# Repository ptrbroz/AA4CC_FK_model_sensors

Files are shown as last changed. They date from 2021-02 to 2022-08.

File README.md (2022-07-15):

# AA4CC_FK_model_sensors

FK_quadrature_decoder - DE0-Nano firmware for quadrature decoding and communication. Also includes folders from PC-side communication (python and matlab)

FK_fpga_shield - shield to be placed upon DE0-Nano

FK_encoder_shield - shield to be connected to each incremental encoder

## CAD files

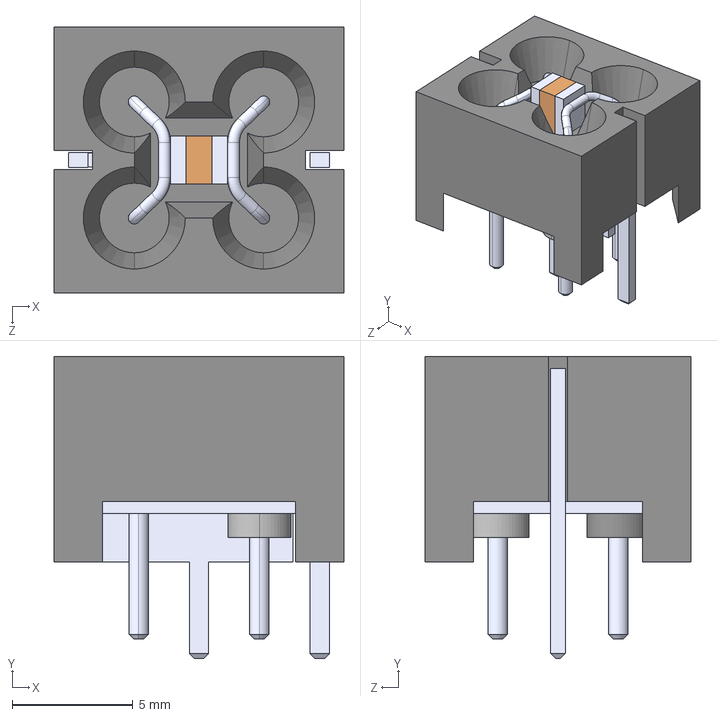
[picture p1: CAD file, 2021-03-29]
FK_fpga_shield/BNX016-01/BNX016-01.step
12.0 x 12.5 x 11.0 mm

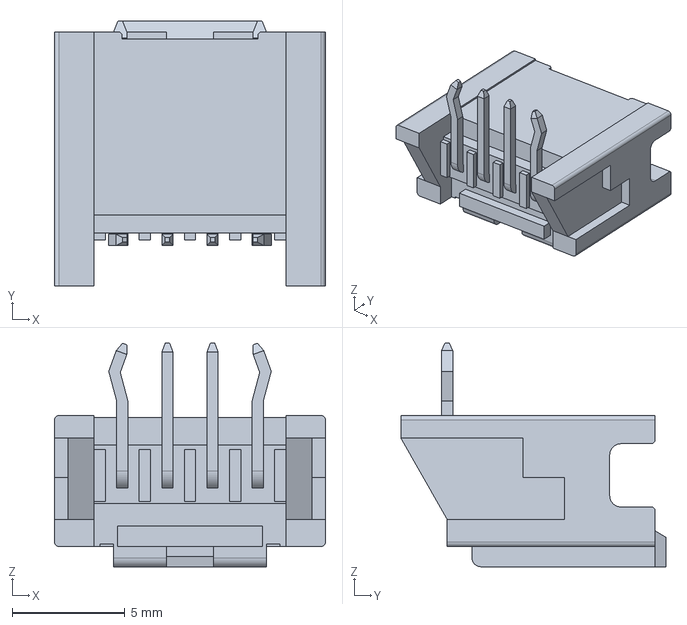
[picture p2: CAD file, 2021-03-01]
FK_fpga_shield/559350430.stp
12.0 x 11.8 x 9.90 mm

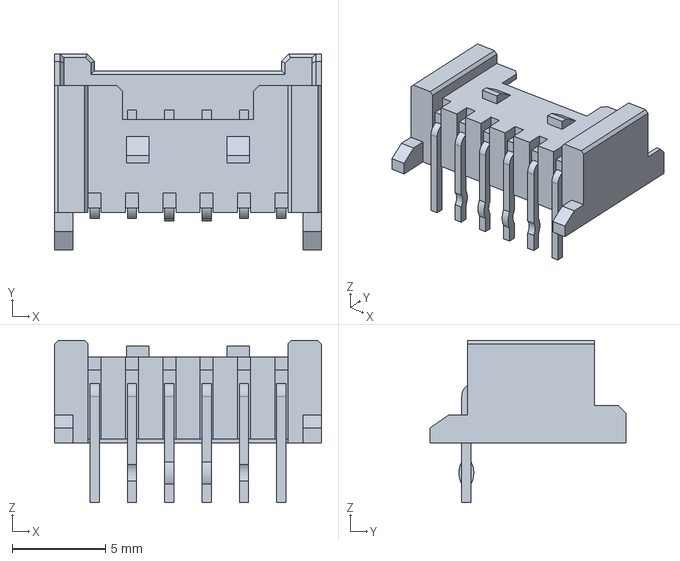
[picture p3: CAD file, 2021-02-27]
FK_fpga_shield/353630660.stp
14.3 x 10.5 x 8.70 mm

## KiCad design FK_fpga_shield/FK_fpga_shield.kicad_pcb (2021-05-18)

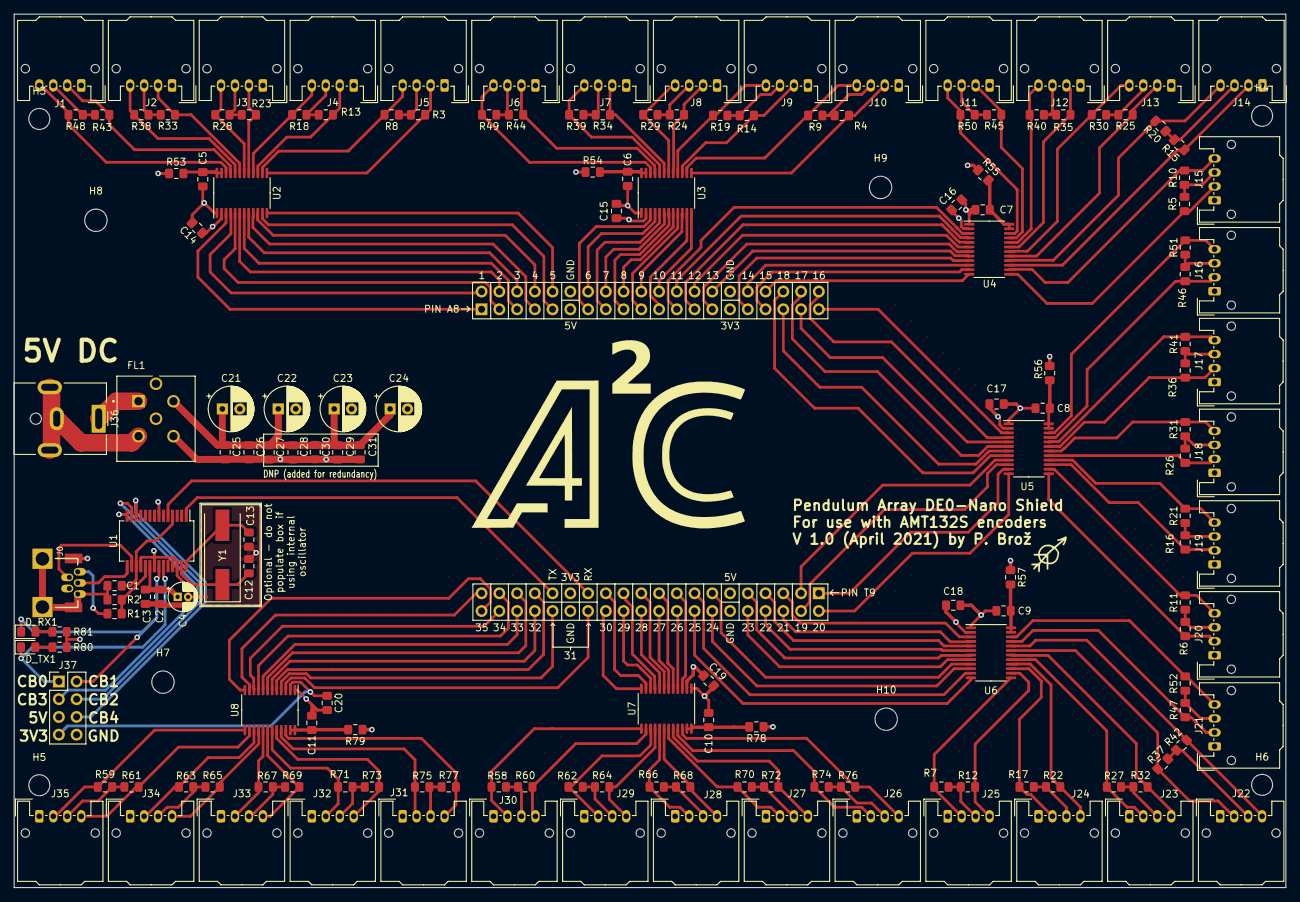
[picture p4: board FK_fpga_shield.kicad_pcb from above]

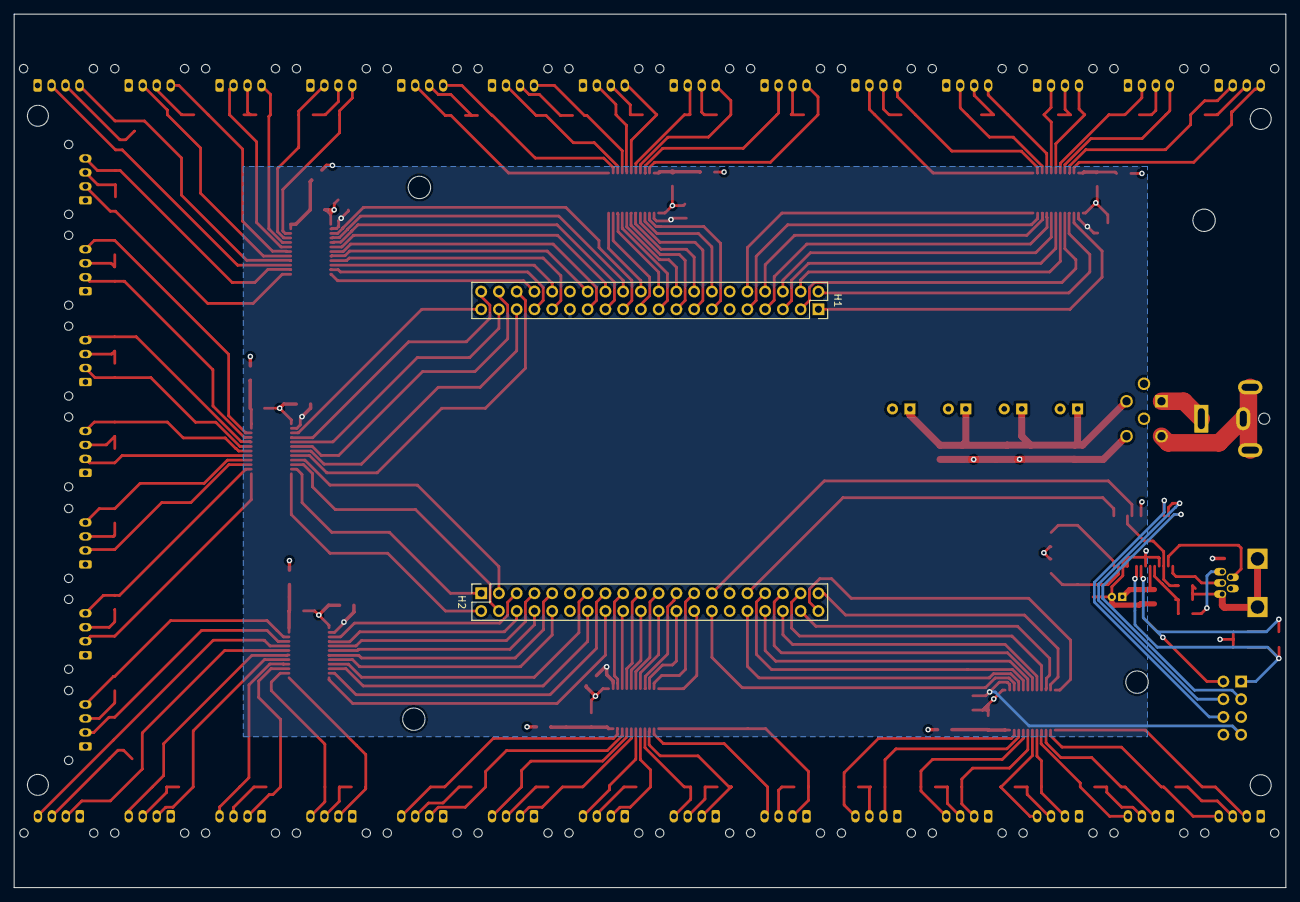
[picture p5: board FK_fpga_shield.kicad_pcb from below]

Board: 4 copper layers, 182.0 x 125.0 mm, 172 parts (2 on the bottom side), 168 nets.

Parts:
C1, C2, C3, C5, C6, C7, C8, C9, C10, C11, C14, C15, C16, C17, C18, C19, C20, C25: 100n; C_0805_2012Metric_Pad1.15x1.40mm_HandSolder
C4: 4.7u; CP_Radial_D4.0mm_P1.50mm
C12, C13: dnp; C_0805_2012Metric_Pad1.15x1.40mm_HandSolder
C21, C22, C23, C24: 22u; CP_Radial_D6.3mm_P2.50mm
C26: 1u_MCC; C_0805_2012Metric_Pad1.15x1.40mm_HandSolder
C27, C28: DNP_10n; C_0805_2012Metric_Pad1.15x1.40mm_HandSolder
C29, C30, C31: DNP_1n; C_0805_2012Metric_Pad1.15x1.40mm_HandSolder
D_RX1: LED RX; LED_0805_2012Metric_Pad1.15x1.40mm_HandSolder
D_TX1: LED_TX; LED_0805_2012Metric_Pad1.15x1.40mm_HandSolder
FL1: BNX016-01; FIL_BNX016-01
H1, H2: Conn_02x20_Odd_Even; PinSocket_2x20_P2.54mm_Vertical
H3, H4, H5, H6: MountingHole; MountingHole_3mm
H7, H8, H9, H10: MountingHole; MountingHole_3.2mm_M3
J0: USB_B_Mini; 54819-0519
J1, J2, J3, J4, J5, J6, J7, J8, J9, J10, J11, J12, J13, J14, J15, J16, J17, J18, J19, J20, J21, J22, J23, J24, J25, J26, J27, J28, J29, J30, J31, J32, J33, J34, J35: molex-51382-0400-microclasp; Molex_MicroClasp_55935-0410_1x04_P2.00mm_Horizontal
J36: Barrel_Jack_MountingPin; BarrelJack_CUI_PJ-063AH_Horizontal
J37: Conn_02x04_Top_Bottom; PinHeader_2x04_P2.54mm_Vertical
R1: 4k7; R_0805_2012Metric_Pad1.15x1.40mm_HandSolder
R2: 10k; R_0805_2012Metric_Pad1.15x1.40mm_HandSolder
R3, R4, R5, R6, R7, R8, R9, R10, R11, R12, R13, R14, R15, R16, R17, R18, R19, R20, R21, R22, R23, R24, R25, R26, R27, R28, R29, R30, R31, R32, R33, R34, R35, R36, R37, R38, R39, R40, R41, R42, R43, R44, R45, R46, R47, R48, R49, R50, R51, R52, R58, R59, R60, R61, R62, R63, R64, R65, R66, R67, R68, R69, R70, R71, R72, R73, R74, R75, R76, R77: 5k6; R_0805_2012Metric_Pad1.15x1.40mm_HandSolder
R53, R54, R55, R56, R57, R78, R79: 200k; R_0805_2012Metric_Pad1.15x1.40mm_HandSolder
R80, R81: 270; R_0805_2012Metric_Pad1.15x1.40mm_HandSolder
U1: FT232RL; SSOP-28_5.3x10.2mm_P0.65mm
U2, U3, U4, U5, U6, U7, U8: nvt2010pw; TSSOP-24_4.4x7.8mm_P0.65mm
Y1: DNP_(12MHz); Crystal_SMD_HC49-SD

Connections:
/1a: H1.2, U2.4
/1b: H1.1, U2.3
/2a: H1.4, U2.6
/2b: H1.3, U2.5
/3V3: C14.2, C15.2, C16.2, C17.2, C18.2, C19.2, C20.1, H1.29, H2.29, J37.7, U2.2, U3.2, U4.2, U5.2, U6.2, U7.2, U8.2
/3a: H1.6, U2.8
/3b: H1.5, U2.7
/4a: H1.8, U2.10
/4b: H1.7, U2.9
/5V: C2.1, C3.1, C4.1, C21.1, C22.1, C23.1, C24.1, C25.1, C26.1, C27.2, C28.2, C29.2, C30.2, C31.2, FL1.2, H1.11, H2.11, J1.3, J2.3, J3.3, J4.3, J5.3, J6.3, J7.3, J8.3, J9.3, J10.3, J11.3, J12.3, J13.3, J14.3, J15.3, J16.3, J17.3, J18.3, J19.3, J20.3, J21.3, J22.3, J23.3, J24.3, J25.3, J26.3, J27.3, J28.3, J29.3, J30.3, J31.3, J32.3, J33.3, J34.3, J35.3, J37.5, R3.1, R4.1, R5.1, R6.1, R7.1, R8.1, R9.1, R10.1, R11.1, R12.1, R13.1, R14.1, R15.1, R16.1, R17.1, R18.1, R19.1, R20.1, R21.1, R22.1, R23.1, R24.1, R25.1, R26.1, R27.1, R28.1, R29.1, R30.1, R31.1, R32.1, R33.1, R34.1, R35.1, R36.1, R37.1, R38.1, R39.1, R40.1, R41.1, R42.1, R43.1, R44.1, R45.1, R46.1, R47.1, R48.1, R49.1, R50.1, R51.1, R52.1, R53.1, R54.1, R55.1, R56.1, R57.1, R58.1, R59.1, R60.1, R61.1, R62.1, R63.1, R64.1, R65.1, R66.1, R67.1, R68.1, R69.1, R70.1, R71.1, R72.1, R73.1, R74.1, R75.1, R76.1, R77.1, R78.1, R79.1, R80.1, R81.1, U1.20
/5a: H1.10, U2.12
/5b: H1.9, U2.11
/6a: H1.14, U3.4
/6b: H1.13, U3.3
/7a: H1.16, U3.6
/7b: H1.15, U3.5
/8a: H1.18, U3.8
/8b: H1.17, U3.7
/9a: H1.20, U3.10
/9b: H1.19, U3.9
/10a: H1.22, U3.12
/10b: H1.21, U3.11
/11a: H1.24, U4.4
/11b: H1.23, U4.3
/12a: H1.26, U4.6
/12b: H1.25, U4.5
/13a: H1.28, U4.8
/13b: H1.27, U4.7
/14a: H1.32, U4.10
/14b: H1.31, U4.9
/15a: H1.34, U4.12
/15b: H1.33, U4.11
/16a: H1.40, U5.4
/16b: H1.39, U5.3
/17a: H1.38, U5.6
/17b: H1.37, U5.5
/18a: H1.36, U5.8
/18b: H1.35, U5.7
/19a: H2.4, U5.10
/19b: H2.3, U5.9
/20a: H2.2, U5.12
/20b: H2.1, U5.11
/21a: H2.6, U6.4
/21b: H2.5, U6.3
/22a: H2.8, U6.6
/22b: H2.7, U6.5
/23a: H2.10, U6.8
/23b: H2.9, U6.7
/24a: H2.14, U6.10
/24b: H2.13, U6.9
/25a: H2.16, U6.12
/25b: H2.15, U6.11
/26a: H2.18, U7.4
/26b: H2.17, U7.3
/27a: H2.20, U7.6
/27b: H2.19, U7.5
/28a: H2.22, U7.8
/28b: H2.21, U7.7
/29a: H2.24, U7.10
/29b: H2.23, U7.9
/30a: H2.26, U7.12
/30b: H2.25, U7.11
/31a: H2.32, U8.4
/31b: H2.28, U8.3
/32a: H2.34, U8.6
/32b: H2.33, U8.5
/33a: H2.36, U8.8
/33b: H2.35, U8.7
/34a: H2.38, U8.10
/34b: H2.37, U8.9
/35a: H2.40, U8.12
/35b: H2.39, U8.11
/RX: H2.27, U1.5
/TX: H2.31, U1.1
GND: C1.2, C2.2, C3.2, C4.2, C5.2, C6.2, C7.2, C8.2, C9.2, C10.2, C11.2, C12.2, C13.2, C14.1, C15.1, C16.1, C17.1, C18.1, C19.1, C20.2, C21.2, C22.2, C23.2, C24.2, C25.2, C26.2, C27.1, C28.1, C29.1, C30.1, C31.1, FL1.4, FL1.5, FL1.6, H1.12, H1.30, H2.12, H2.30, J0.5, J0.6, J1.1, J2.1, J3.1, J4.1, J5.1, J6.1, J7.1, J8.1, J9.1, J10.1, J11.1, J12.1, J13.1, J14.1, J15.1, J16.1, J17.1, J18.1, J19.1, J20.1, J21.1, J22.1, J23.1, J24.1, J25.1, J26.1, J27.1, J28.1, J29.1, J30.1, J31.1, J32.1, J33.1, J34.1, J35.1, J37.8, R2.2, U1.7, U1.18, U1.21, U1.25, U1.26, U2.1, U3.1, U4.1, U5.1, U6.1, U7.1, U8.1
unnamed: C1.1, U1.4, U1.17
unnamed: C5.1, R53.2, U2.23, U2.24
unnamed: C6.1, R54.2, U3.23, U3.24
unnamed: C7.1, R55.2, U4.23, U4.24
unnamed: C8.1, R56.2, U5.23, U5.24
unnamed: C9.1, R57.2, U6.23, U6.24
unnamed: C10.1, R78.2, U7.23, U7.24
unnamed: C11.1, R79.2, U8.23, U8.24
unnamed: C12.1, U1.27, Y1.1
unnamed: C13.1, U1.28, Y1.2
unnamed: D_RX1.1, J37.2, U1.22
unnamed: D_RX1.2, R81.2
unnamed: D_TX1.1, J37.1, U1.23
unnamed: D_TX1.2, R80.2
unnamed: FL1.1, J36.1
unnamed: FL1.3, J36.2, J36.MP
unnamed: J0.1, R1.1
unnamed: J0.2, U1.16
unnamed: J0.3, U1.15
unnamed: J1.2, R43.2, U2.21
unnamed: J1.4, R48.2, U2.22
unnamed: J2.2, R33.2, U2.19
unnamed: J2.4, R38.2, U2.20
unnamed: J3.2, R23.2, U2.17
unnamed: J3.4, R28.2, U2.18
unnamed: J4.2, R13.2, U2.15
unnamed: J4.4, R18.2, U2.16
unnamed: J5.2, R3.2, U2.13
unnamed: J5.4, R8.2, U2.14
unnamed: J6.2, R44.2, U3.21
unnamed: J6.4, R49.2, U3.22
unnamed: J7.2, R34.2, U3.19
unnamed: J7.4, R39.2, U3.20
unnamed: J8.2, R24.2, U3.17
unnamed: J8.4, R29.2, U3.18
unnamed: J9.2, R14.2, U3.15
unnamed: J9.4, R19.2, U3.16
unnamed: J10.2, R4.2, U3.13
unnamed: J10.4, R9.2, U3.14
unnamed: J11.2, R45.2, U4.21
unnamed: J11.4, R50.2, U4.22
unnamed: J12.2, R35.2, U4.19
unnamed: J12.4, R40.2, U4.20
unnamed: J13.2, R25.2, U4.17
unnamed: J13.4, R30.2, U4.18
unnamed: J14.2, R15.2, U4.15
unnamed: J14.4, R20.2, U4.16
unnamed: J15.2, R5.2, U4.13
unnamed: J15.4, R10.2, U4.14
unnamed: J16.2, R46.2, U5.21
unnamed: J16.4, R51.2, U5.22
unnamed: J17.2, R36.2, U5.19
unnamed: J17.4, R41.2, U5.20
unnamed: J18.2, R26.2, U5.17
unnamed: J18.4, R31.2, U5.18
unnamed: J19.2, R16.2, U5.15
unnamed: J19.4, R21.2, U5.16
unnamed: J20.2, R6.2, U5.13
unnamed: J20.4, R11.2, U5.14
unnamed: J21.2, R47.2, U6.21
unnamed: J21.4, R52.2, U6.22
unnamed: J22.2, R37.2, U6.19
unnamed: J22.4, R42.2, U6.20
unnamed: J23.2, R27.2, U6.17
unnamed: J23.4, R32.2, U6.18
unnamed: J24.2, R17.2, U6.15
unnamed: J24.4, R22.2, U6.16
unnamed: J25.2, R7.2, U6.13
unnamed: J25.4, R12.2, U6.14
unnamed: J26.2, R74.2, U7.21
unnamed: J26.4, R76.2, U7.22
unnamed: J27.2, R70.2, U7.19
unnamed: J27.4, R72.2, U7.20
unnamed: J28.2, R66.2, U7.17
unnamed: J28.4, R68.2, U7.18
unnamed: J29.2, R62.2, U7.15
unnamed: J29.4, R64.2, U7.16
unnamed: J30.2, R58.2, U7.13
unnamed: J30.4, R60.2, U7.14
unnamed: J31.2, R75.2, U8.21
unnamed: J31.4, R77.2, U8.22
unnamed: J32.2, R71.2, U8.19
unnamed: J32.4, R73.2, U8.20
unnamed: J33.2, R67.2, U8.17
unnamed: J33.4, R69.2, U8.18
unnamed: J34.2, R63.2, U8.15
unnamed: J34.4, R65.2, U8.16
unnamed: J35.2, R59.2, U8.13
unnamed: J35.4, R61.2, U8.14
unnamed: J37.3, U1.14
unnamed: J37.4, U1.13
unnamed: J37.6, U1.12
unnamed: R1.2, R2.1, U1.19

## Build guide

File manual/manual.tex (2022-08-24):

\documentclass[twoside]{article}
\usepackage[a4paper]{geometry}
\geometry{verbose,tmargin=2.5cm,bmargin=2cm,lmargin=2cm,rmargin=2cm}
\usepackage{fancyhdr}
\pagestyle{fancy}

\usepackage{lmodern}
\usepackage[T1]{fontenc}
\usepackage[cp1250]{inputenc}
\usepackage{amsmath}
\usepackage{amsfonts} 
\usepackage{bm} 

\newcommand\abs[1]{\left|#1\right|}
\newcommand{\res}{\text{res}}
\newcommand{\LH}{\stackrel{LH}{=}}
\newcommand{\FT}{\hat{=}}
\newcommand{\TF}{\check{=}}
\renewcommand\Re[1]{\operatorname{Re}\{#1\}}
\renewcommand\Im[1]{\operatorname{Im}\{#1\}}

\usepackage{url}

\usepackage{multirow}

\usepackage{subcaption}
\usepackage{indentfirst}

\usepackage{graphicx} 
\usepackage{epstopdf}

\usepackage[unicode=true, bookmarks=true,bookmarksnumbered=true,
bookmarksopen=false, breaklinks=false,pdfborder={0 0 0},
pdfpagemode=UseNone,backref=false,colorlinks=true] {hyperref}

\usepackage{xkeyval}	% Inline todonotes
\usepackage[textsize = footnotesize]{todonotes}
\presetkeys{todonotes}{inline}{}

\renewcommand{\theenumi}{\alph{enumi}}

\fancyhf{}
\usepackage{titling}
\fancyhf[HC]{}
\fancyhf[HLE,HRO]{\thetitle}
\fancyhf[HRE,HLO]{\today}

\fancyhf[FLE,FRO]{\thepage}

% �daje o autorovi
\title{FK Quadrature Decoder Manual}
\author{Petr Bro�}
\date{\today}

\begin{document}

\maketitle

\tableofcontents

\newpage

\section{Intro}

This document describes the FK quadrature decoder device, developed at CTU FEE to read an array of up to 35 incremental encoders. The device consists of a DE0-Nano fpga kit, a pcb shield mounted onto the fpga and cables connecting the pcb shield to individual encoders. Both the pcb design and the vhdl code used to program the fpga kit are available from a github repository\footnote{https://github.com/ptrbroz/AA4CC\_FK\_model\_sensors}. 

The document will be split into two parts -- first being a User manual, which will describe how to set up and communicate with the device. It will be followed by a Technical manual, which is meant to aid in extending or modifying the device. It will describe the hardware and cabling, and also roughly sketch out the workings of the fpga program. 

The device uses exclusively positive numbers; when this document uses the word \emph{integer}, interpret it as \emph{unsigned integer} unless explicitly stated otherwise.

\section{User manual}

\subsection{Setting up}

To set up the device, follow theese steps:

\begin{enumerate}
\item If your DE0-Nano is not yet programmed, compile the quartus project and flash it into DE0-Nano. You need to program the serial configuration device, otherwise the program won't persist through a power cycle -- see DE0-Nano user manual for instructions\footnote{https://www.ti.com/lit/ug/tidu737/tidu737.pdf, page 146}.
\item Mount the PCB shield onto the fpga kit. To determine orientation, make sure that the usb connector on the pcb and the usb connector on the fpga kit both point in the same direction. You can also make use of the pcb silkscreen (locations of pins A8 and T9 of the fpga kit are printed on it).
\item Make sure that no usb cable is connected to the fpga kit itself.
\item Connect the incremental encoders to the connectors located at the edges of the pcb shield.
\item Connect a 5V DC power source via the barrel jack.
\item Connect the pcb shield to your computer via the mini-usb port located next to the barrel jack.
\end{enumerate}

\subsection{Turning off the device}
\label{turnoff}

Ideally, when turning off the device, unplug the usb cable first and only then unplug the 5V power adapter.

Alternatively, it is enough to turn off the computer to which the usb cable is connected instead of unplugging it (if the usb port to which it connects turns off with the computer).

Due to an oversight in the pcb design, unpluggin the 5V power source while a usb cable is connected places the FT232R (uart-usb converter) chip outside its maximum ratings. 

A solution (which eliminates the need to unplug cables in specific order) to this oversight is described in \ref{hwbug}.

\newpage{}

\subsection{Communication}

\par The device communicates with the user via bidirectional UART with following parameters: Baudrate 230400, 8 data bits, no parity. Apart from going to the usb-serial converter IC, the fpga's transmit line is also routed to pin B16 (located on the bottom gpio header)\footnote{I reccomend this site for locating pins on DE0-Nano: https://sites.google.com/site/fpgaandco/de0-nano-pinout} where a oscilloscope probe can be attached for inspection.

Upon powerup, the device will not be sending any data -- it needs to be configured first.

\subsubsection{User to device communication}

There are three types of commands the user can send to the device. Two of them consist of only a single byte that the user needs to send:

\begin{enumerate}
\item \textbf{COMMS ON} -- sending the byte 0x04 causes the device to start transmitting data, using it's current settings.
\item \textbf{COMMS OFF} -- sending the byte 0x02 causes the device to stop transmitting data.
\item \textbf{CONFIGURE} -- see below.
\end{enumerate}

The \textbf{CONFIGURE} command consists of 7 bytes. It is used to choose which encoders will be reported by the device, at what resolution, how often, and lastly it allows the positions of the encoders to be reset. Upon receiving the configure command, the device will send a reply (see next section), reconfigure itself and start transmitting data.

The first nibble of the first byte encodes the desired revolution counter bit-depth. When set to 0, the device does not report the number of revolutions. The second nibble of the first byte must be 0x1. 

The remaining 6 bytes are best thought of as an array of bits. The first 35 bits form the encoder enable vector -- when a bit in the enable vector is set to one, the corresponding encoder's position (and possibly number of revolutions) will be reported\footnote{The encoder connectors on the pcb are enumerated clockwise, starting next to the barrel jack. Their numbers are also printed on the silkscreen as JX, where X is the number.}. Bits 36 to 39 form an unsigned integer, used to represent the desired position resolution in bits. Bit 40 is the position  reset bit -- when it is set to one, all positions will be reset to their default value of $2^{r-1}$, where $r$ denotes the position resolution in bits. The last 8 bits form another unsigned integer, this time representing the minimum time the device should wait between sending its messages, in milliseconds.

\textbf{Example: Configure command}

\begin{figure}[htb]
	\centering
	
	\caption{Configure command illustration}
	\label{fig:config}
\end{figure}

The figure on this page illustrates how the configure command is assembled. The values show therein are choosen to configure the device to:

\begin{itemize}
\item Set revolution counter bit depth to 5 bits
\item Enable reading encoders 1 through 10 and 26 through 35
\item Disable reading encoders 11 through 25
\item Read them using a resolution of 12 bits
\item Reset the position counters.
\item Transmit data once every 10 milliseconds.
\end{itemize}

To achieve theese settings, the user needs to send following bytes (in this order) to the device: 0x51, 0xFF, 0xC0, 0x00, 0x7F, 0xF9, 0x0A.

\subsubsection{Settings constraints}

Following settings are valid:

\begin{itemize}
\item \textbf{Encoder enable vector} -- Any combination of ones and zeros.
\item \textbf{Position resolution} -- Any integer from 1 to 13. If a zero is sent, it will be interpreted as one. 13 is the maximum resolution used within the device -- while resolution options of 14 and 15 bits are also supported, they only pad the sent data with zeros and you shouldn't use them unless you know exactly why you're doing it. (See TODO)
\item \textbf{Revolution counter bit depth} -- Any integer from 0 to 7. Setting a zero disables revolution reporting altogether. If a value greater than 7 is sent, it will be reduced to 7.
\item \textbf{Reset bit} -- Either 1 or 0.
\item \textbf{Minimum time between messages} -- Any integer between 0 and 255. Be aware that this is the minimum time -- the actual time between messages will always be at least as long as it takes to transmit all the data. Formula for minimum time it takes to transmit (assuming revolution data is not sent): $(ceil(\frac{(r+1)\cdot{}E}{8}) + 3)\cdot{}\frac{10}{B}$, where r is resolution in bits, E is the number of enabled encoders and B is Baud = 230400. If revolution data is enabled, the minimum time will increase to  $(ceil(\frac{4+(r+R+2)\cdot{}E}{8}) + 3)\cdot{}\frac{10}{B}$, where R is the revolution counter bit depth.
\end{itemize}

\subsubsection{Device to user communication}

The device can send two types of messages to the user. Both begin with a header consisting of 3 bytes and are then followed by a number of data bytes. Reserved separator bits are inserted into the data to ensure that the byte pattern of a header does not occur within the data -- allowing for clear identification of the beginning of a message in incoming bytes.\footnote{This rule is broken if you set the resolution to 14 or 15 bits.} \\

\noindent\emph{\textbf{Configure reply message}}

This message is sent only as a reply to the configure command sent by the user. It's header always consists of bytes 0xff, 0xff, 0xf0 in this order. Following them are 7 data bytes -- those carry within them the same array of 48 bits that the user provided in their configure command, with the exception that the first bit of each data byte is instead reserved as a separator bit and is always zero.

The configure reply message does not currently report the revolution counter bit depth.

\textbf{Example: Config reply message}
\begin{figure}[h!]
	\centering
	
	\caption{Configure reply illustration (Only first 5 bytes are shown)}
	\label{fig:JpgEpsCompare}
\end{figure}

The figure above illustrates how a reply to the configuration reply message to the message show in figure \ref{fig:config} would begin. \\\\

\noindent{}\emph{\textbf{Data message (without revolutions)}}

This section assumes that revolution counter bit depth is set to zero, meaning that revolution data is not reported by the device. See below for how the message changes when revolutions are reported.

This is the most important message -- it is used by the device to report the positions of encoders to the user.

The header of this message is a little more complex, as it carries data. Its first byte is always 0xff, its second byte is one of \{0xfc, 0xfd, 0xfe, 0xff\}, and its last byte can have many different values. When viewed as an array of 24 bits, it can be parsed thus:

\newpage{}
\begin{itemize}
\item Bits 1 to 14 -- Reserved, will always be ones.
\item Bits 15 to 20 -- Integer representing how many encoders are enabled
\item Bits 20 to 24 -- Integer representing the resolution in bits
\end{itemize}

The purpose of the reserved bits is to facilitate identification of the beginning of the message. Due to presence of separator bits (which are always zero) and maximum position resolution being 13 bits, the only situation in which 14 consecutive ones appear in data sent by the device is a message beginning.

The header is followed by a number of data bytes, which carry the positions of each enabled encoder. Each position is sent as an integer preceded by a separator bit (which will always be zero). Thus the number of bytes you should expect can be calculated after parsing the header as $ceil(\frac{(r+1)\cdot{}E}{8})$, where r is resolution in bits and E is the number of enabled encoders. The positions are sent starting in ascending order of encoder indices.

The number of encoders and resolution should fall within certain constraints. In particular, the number of enabled encoders needs to be at most 35, and the resolution needs to be between 1 and 15 bits, otherwise the 3 bytes do not form a valid data message header. Note that the header for Config reply message appears as 63 encoders running at resolution of zero bits, and thus can be differentiated from data message headers.

\textbf{Example: Data message (revolution reporting disabled)}
\begin{figure}[h]
	\centering
	
	\caption{Data message illustration}

\end{figure}

Figure above shows what a data message might look like. Upon parsing the header, the user computer performs the calculation $\frac{(6+1)\cdot{}3}{8} \approx 2.6$. Rounding (always) up, we arrive at 3 -- the number of data bytes we need to receive. The last 3 bits of the third data byte do not carry any information.

Reading the positions, we see that the third encoder is in the default position, encoder number one has moved somewhat in one direction from the default and number two has moved significantly in the opposite direction.

Note that there is no indication of the actual index of the encoders -- the user needs to keep in mind which encoders they have enabled. The message above might represent the positions of encoders 1, 2 and 3. But it may also represent the positions of encoders 5, 26 and 31, if those happen to be the ones that are enabled.

\noindent{}\emph{\textbf{Data message (with revolutions reported)}}

Currently, it is not possible to differentiate between data messages with revolutions and without revolutions based just on the initial header. It is recommended for the user to note if they configured revolution counter bit depth to a nonzero value and to expect messages with revolution data if they did so.

When revolution counter bit depth is nonzero, the positions data is followed by a section of revolution data. The data section is the same as in case of data message without revolutions (see above).

The revolution data section begins with a secondary header consisting of 4 bits which encode the revolution counter bit depth used. Following the header is an array of bits in a similar format to the positions section: each revolution counter is preceded by a separation bit (always zero). Thus revolutions reporting prolongs the data message by 4+(1+R)*E bits, where R is is the revolution counter bit depth and E is the number of encoders.

The total number of bytes of the data message with revolutions is calculated as  $ceil(\frac{4+(r+R+2)\cdot{}E}{8})$, where r is the position resolution. 

Revolutions are represented as integers with offset zero. No revolutions corresponds to a value of $2^R$. This value is incremented whenever the position of the encoder in question overflows and decremented whenever it underflows.

\begin{figure}[h]
	\centering
	
	\caption{Data message illustration}
\label{fig:3}
\end{figure}

Example message is shown in figure \ref{fig:3}. Note that due to the zero offset, counter value of 6 for encoder 1 should be interpreted as that encoder performing a sum of two revolutions in one direction, while encoder 2 (counter value 3) has performed a sum of one revolution in the opposite direction. A counter value of 4 would correspond to a sum zero revolutions.

\newpage{}
\subsection{Communications demo}

\noindent{}A terminal demo script written in python is located within this repository:\\ FK\_quadrature\_decoder\textbackslash{}python\textbackslash{}CommDemo.py.

The script consists of utilities for conversion between bytes and lists of bits, as well as a function that initialises the device with desired settings and another that parses its reply. The parsing of data messages is done in a loop in the program itself.

When using the script, you may experience bytes being discarded if you set the minimum time between messages too low. In my testing, this problem appeared to be closely related to the ammount of information printed into the terminal, as well as to whether my pc was performing other intensive operations, and would lessen or disappear altogether when I redirected the script's output into a log instead of printing it to terminal. This leads me to believe that it is a fault of the computer rather than of the device; I'm guessing it's caused by a buffer overflowing somewhere. 

The script also does not (at the time of writing) check for validity of incoming data message headers.

The script was tested on windows 10 machines, using Windows Terminal\footnote{https://github.com/microsoft/terminal} (default windows cmd does not support the return codes needed to redraw multiple lines of data).

\subsection{Reconfiguring on the fly}

As a last note: the device keeps count of the positions of all  encoders at all times; not just the ones that are currently enabled for reporting. You can, therefore, begin your experiment with only some of the encoders enabled and switch to a different set of enabled encoders later -- no position reset is necessary.

\newpage{}
\section{Various technical details}

You don't need to read any further unless you're planning to modify or extend the firmware or hardware of the device.

\subsection{Cabling}

The cable used for interconnecting the pcb shield and the AMT132S encoders is 24AWG, 4-wire UTP. Wire gauge selected as only intersection that's within specs of crimp terminals on both sides.

The cable is terminated with a microclasp connector on one side and a zpd connector on the other. Since the encoders use a 18-path zpd connector (which was not available for purchase), 20-path zpd connectors cut down with a hobby knife are used instead.

\begin{figure}[h!]
	\centering
	\begin{subfigure}[b]{0.45\textwidth}
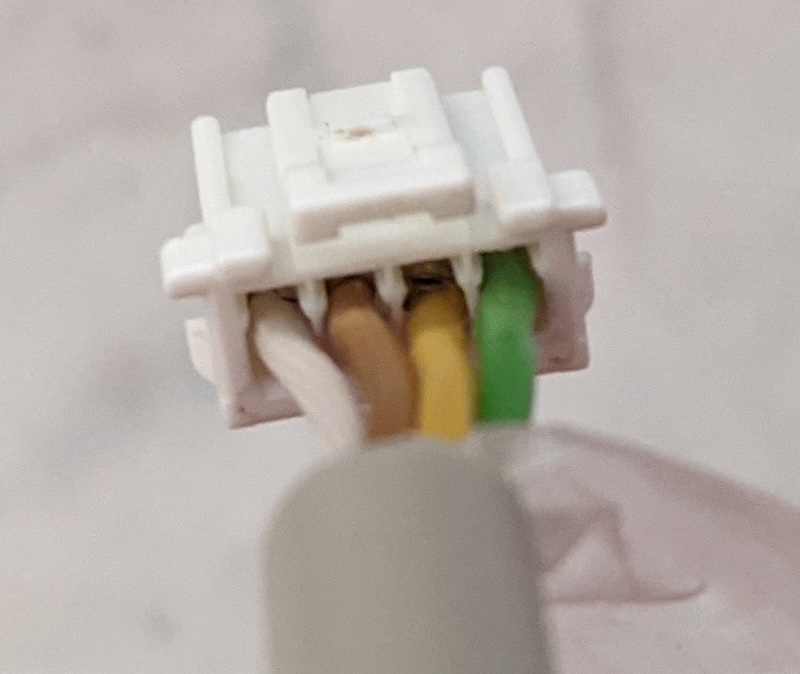
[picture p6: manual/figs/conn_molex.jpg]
		
		\caption{Molex microclasp connector}
		\label{fig:molex}
	\end{subfigure}
	\begin{subfigure}[b]{0.45\textwidth}
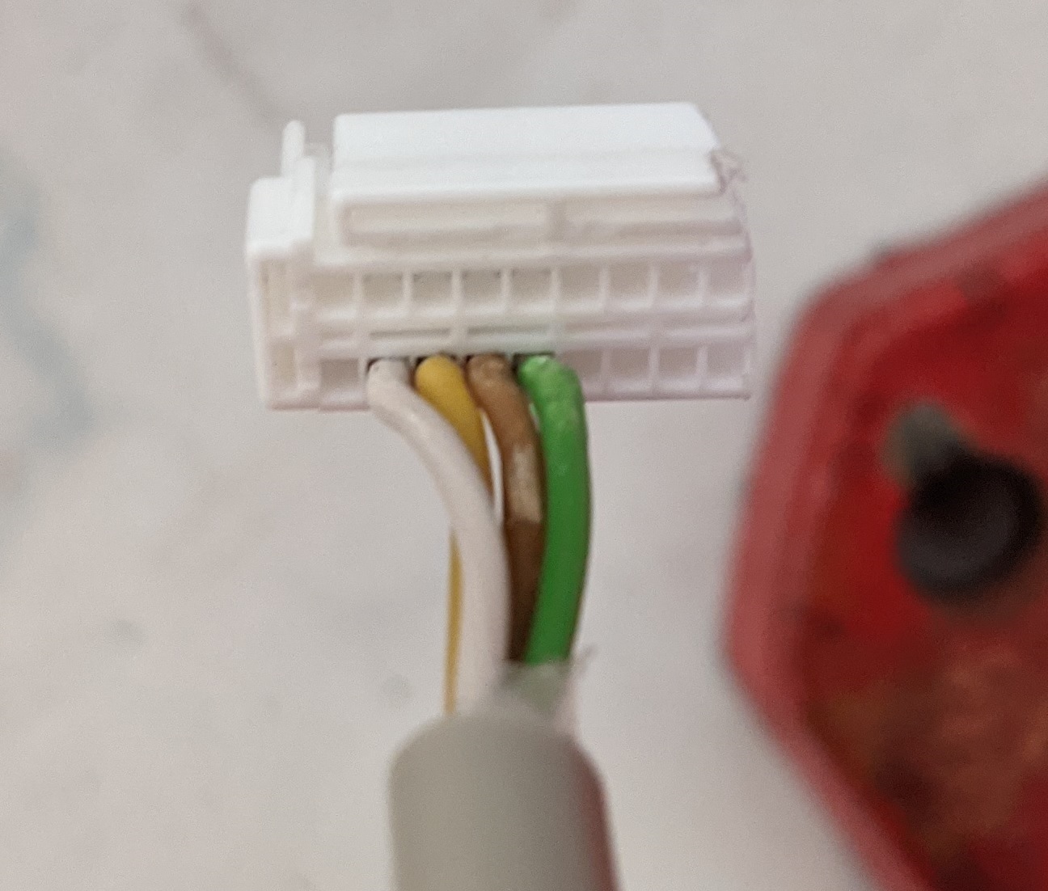
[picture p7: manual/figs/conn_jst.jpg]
		
		\caption{JST zpd connector}
		\label{fig:jst}
	\end{subfigure}
	\caption{Cable connectors}
	\label{fig:JpgEpsCompare}
\end{figure}

The figure above shows how the wires are assigned to individual sockets of the connectors. In the photos, the wires are: 

\begin{itemize}
\item White = GND
\item Brown = Quadrature channel A
\item Yellow = +5V
\item Green = Quadrature channel B
\end{itemize}

The pairs of wires used are choosen to ensure that the quadrature channels are not twisted together.

\noindent\textbf{A note on cable assembly:} Crimping the SZPD-002T-P0.3 contacts and inserting them into the zpd housings is challenging and frustrating -- if you happen to have an idle buddhist monk at hand, this would be an ideal job to assign to them. When using the 22 AWG crimping tool I found in the lab, I had to finish the job with a pair of pliers every time, and the results were not great. Maybe try to find a 24AWG tool and/or look for a jst crimping tool\footnote{Connector datasheet http://www.farnell.com/datasheets/2261947.pdf lists some industrial-looking crimping machines.}.

\subsection{PCB bug (turning off & FT232)}
\label{hwbug}

There is an error in the the pcb design, necessitating a specific order in which the power and usb cables can be unplugged from the device when turning it off, as described in \ref{turnoff}. 

To fix this issue, 3 components need to be added to the pcb - two resistors (80k, 4k) and a generic NPN transistor. Those components, as well as their placement in the circuit, have been added to the kicad schematic of the PCB (see blue box next to the FT232 symbol).

If you don't want to add the components to the PCB itself, you can still solve the problem (we have solved it this way). To solder the components, you will need to make use of pads originally intended for the R1 resistor (which is now left unpopulated, see schematic). The third needed solder point is the 5V power rail. This is easily accesible via the unpopulated J37 2x4 connector, next to the usb connector.

\subsection{Firmware structure}

The fpga firmware is provided as a quartus II project. The design is split into several entities:

\subsubsection{FK quadrature decoder}

This is the top-level entity, dealing with interconnections between all other entities and with GPIO mappings.

\subsubsection{Uart TX / Uart RX}

Simple entities implementing uart transmitter and receiver. Input/output is a single byte, buffering etc. is handled in other entities.

\subsubsection{Uart out manager}

This entity takes a series of bytes and feeds them in order into the Uart TX entity, which transmits them. The bytes are provided to the manager either by the Watcher or by the Boss entity, with Boss entity having precedence.

\subsubsection{Boss}

This entity receives and interprets communication from the user into the fpga, and is also responsible for changing configuration of the Watcher entity when a config message is received from the user. Additionally, it also creates the config reply message and passes it to Uart out manager.

\subsubsection{Watcher}

This entity is responsible for periodically sampling all connected quadrature encoders and assembling data messages (which it passes to uart out manager). It holds within itself an array of 35 Quadrature Decoder Pb entities. The parameters of the data message (such as resolution or which encoders are reported) as well as the frequency with which data messages are created is governed by inputs driven by the Boss entity.

\subsubsection{Quadrature Decoder Pb}

This is a simple entity handling the decoding of quadrature signals for a single encoder. It takes in the two quadrature signals and outputs position and number of resolutions (to the Watcher entity).

\end{document}

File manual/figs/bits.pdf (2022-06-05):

0 1 0 1 0 0 0 1 | 1 1 1 1 1 1 1 1 | 1 1 0 0 0 0 0 0 | 0 0 0 0 0 0 0 0 | 0 1 1 1 1 1 1 1 | 1 1 1 1 1 0 0 1 | 0 0 0 0 1 0 1 0

This nibble is always 0x1

Enable reading
encoder #1 Enable reading
encoder #10
| | Disable reading encoder #11

Disable reading
encoder #25

Disable reading
encoders #17 to #24

Enable reading
encoder #35

Use resolution of
12 bits

Do reset
positions

Send a message
every 10ms

Set rev. counter
bit depth 5

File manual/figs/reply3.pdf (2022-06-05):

1 1 1 1 1 1 1 1 | 1 1 1 1 1 1 0 0 | 0 0 1 0 0 1 1 0 | 0 0 1 1 1 1 1 0 | 1 0 1 0 1 0 0 0

First 14 bits of header
are reserved ones

Separator bit

Number of enabled
encoders = 2

Resolution
= 6 bits

Position 1
= 31

Separator bit

Position 2
= 42
1 1 0 1 1 0 0 0 1 1 0 0 0 0 0 0

Revolution
bit depth = 3

Separator bits

Rev. cnt. 1
= 6

Rev. cnt. 2
= 3

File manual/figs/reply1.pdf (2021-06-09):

1 1 1 1 0 0 0 0 | 0 1 1 1 1 1 1 1 | 0 1 1 1 0 0 0 0

Enable reading
| encoder #1
1 1 1 1 1 1 1 1 | 1 1 1 1 1 1 1 1

Header bytes are always
0xff 0xff 0xf0 | Enable reading
encoder #8
| | Disable reading encoder #11
Separator bit | Separator bit

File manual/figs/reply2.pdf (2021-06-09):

1 1 1 1 1 1 1 1 | 1 1 1 1 1 1 0 0 | 0 0 1 1 0 1 1 0 | 0 0 1 1 1 1 1 0 | 1 0 1 0 1 0 0 1

First 14 bits of header
are reserved ones

Separator bit

Number of enabled
encoders = 3

Resolution
= 6 bits

Position 1
= 31

Separator bit

Position 2
= 42
0 0 0 0 0 0 0 0

Separator bit

Position 3
= 32

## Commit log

2021-02-27 pre conn symbol rework
    [548190519.stp, FK_fpga_shield.kicad_pcb, FK_fpga_shield.sch]
2021-02-27 pre symbol update
    [FK_fpga_shield.sch]
2021-02-27 replace conn symbol on encoder shield
    [FK_encoder_shield.sch]
2021-02-27 change connector sym/footprint on fpgashield
    [353630660.stp, FK_fpga_shield.kicad_pcb, FK_fpga_shield.sch]
2021-03-01 change connector to microclasp 4 wire
    [559350430.stp, FK_encoder_shield.kicad_pcb, FK_encoder_shield.sch, FK_fpga_shield.kicad_pcb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]
2021-03-01 add bom prep
    [bom_nastrel_fkmodel.ods]
2021-03-01 single level shifter schema
    [FK_fpga_shield.sch]
2021-03-01 WIP fpga shield layout
    [FK_fpga_shield.sch]
2021-03-01 wip lazyour (mapped to header)
    [FK_fpga_shield.kicad_pcb, FK_fpga_shield.sch]
2021-03-03 wip route before U4,U6 move
    [FK_fpga_shield.kicad_pcb]
2021-03-03 levelshifter to fpga signals routed
    [FK_fpga_shield.kicad_pcb, FK_fpga_shield.sch]
2021-03-03 fix u6
    [FK_fpga_shield.kicad_pcb]
2021-03-03 wip routing (usb done (?))
    [FK_fpga_shield.kicad_pcb, FK_fpga_shield.sch]
2021-03-04 decouple 3V3 references just in case
    [FK_fpga_shield.kicad_pcb, FK_fpga_shield.sch]
2021-03-05 redo 3v3 routing
    [FK_fpga_shield.kicad_pcb, FK_fpga_shield.sch]
2021-03-06 switch to 3V3 bottom layer plane, begin silkscreen
    [FK_fpga_shield.kicad_pcb]
2021-03-06 silkscreen: main header
    [FK_fpga_shield.kicad_pcb]
2021-03-06 silkscreen cosmetic fixes
    [FK_fpga_shield.kicad_pcb]
2021-03-06 various silkscreen cometics
    [FK_fpga_shield.kicad_pcb]
2021-03-08 choosen choke
    [FK_fpga_shield.kicad_pcb, FK_fpga_shield.sch]
2021-03-08 2x4 breakout header for uart convertor, choke laid out
    [FK_fpga_shield.kicad_pcb, FK_fpga_shield.sch]
2021-03-29 replace common mode choke with filter
    [BNX016-01.step, FK_fpga_shield.kicad_pcb, FK_fpga_shield.sch]
2021-04-05 restore schematic from last version
    [FK_fpga_shield.sch]
2021-04-07 various minor
    [FK_fpga_shield.kicad_pcb, FK_fpga_shield.sch]
2021-04-08 mounting holes, silkscreen
    [FK_fpga_shield.sch]
2021-04-08 silkscrn fix
    [FK_fpga_shield.kicad_pcb]
2021-04-09 gerbers etc
    [FK_fpga_shield-B_Cu.gbl, FK_fpga_shield-B_Mask.gbs, FK_fpga_shield-B_Paste.gbp, FK_fpga_shield-B_SilkS.gbo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]
2021-04-09 remove unused encoder shield folder
    [353630660.stp, 559350430.stp, FK_encoder_shield.kicad_pcb, FK_encoder_shield.sch]
2021-05-18 generate gerbers
    [FK_fpga_shield-B_Cu.gbl, FK_fpga_shield-B_Mask.gbs, FK_fpga_shield-B_Paste.gbp, FK_fpga_shield-B_SilkS.gbo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]
2021-05-26 pin assignments, update gitignore
    rtl viewer still looking kinda wonky, maybe try to toss buffer type and return to output in watcher?
2021-06-02 wip fixing printing-related bug
2021-06-07 rename generated wires
2021-06-09 add wip manual
    [bom_nastrel_fkmodel.ods]
2021-06-23 turning off
    [FK_fpga_shield.sch]
2022-01-26 watcher logic for revolution printing
2022-01-26 fix wire len
2022-07-14 wip - this version simulates via code generation and seems to receive data from device
2022-08-16 Add feature: setting zero communication period now switches device to single message mode. In this mode, data messages are not sent periodically. Instead, they are sent only when requested by user (w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
2022-08-24 manual update (add pcb bug fix description, add firmware structure overview)
2022-10-03 pcb update for new kicad
